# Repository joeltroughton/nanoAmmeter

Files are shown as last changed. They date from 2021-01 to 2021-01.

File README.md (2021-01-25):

# nanoAmmeter

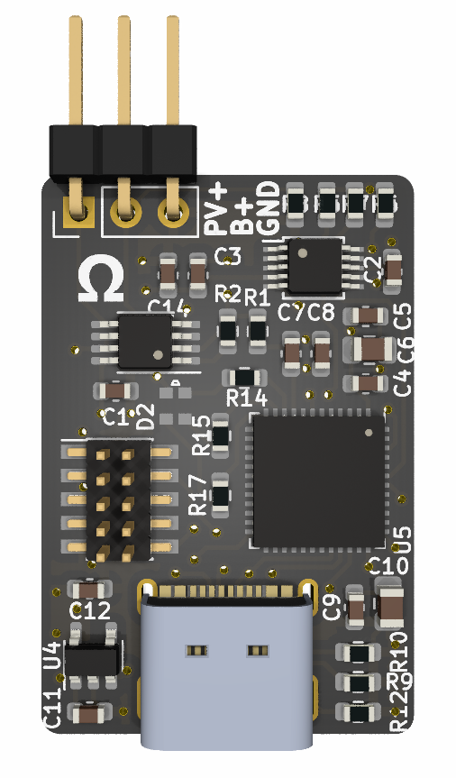
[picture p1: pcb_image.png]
nanoAmmeter


nanoAmmeter is a small research device designed to measure the voltage applied to, and the current flowing through biological glucose sensors on the order of 10s to 100s of nanoamps.

As glucose is detected by the sensor, its resistance changes. nanoAmmeter measures the current flow through the sensor for later analysis.

## Function

The nanoAmmeter is inserted between the biosensor's negative electrode and ground. The voltage drop across a 100kOhm resistor is amplified by a gain of 101 by a very low offset opamp (Analog LTC2055, ± 3 μV) and finally read by a 16-bit ADC (TI ADS1115). With a FSR of 4.096V, this gives us a theoretical current resolution of 12.4 pA. 

The voltage applied to the positive side of the biosensor is buffered to the ADC with unity gain for a theoretic voltage resolution of 125 μV.

The ADC is read by a STM32F072 MCU at 128 samples per second where it is fed into a finite impulse response, low pass filter and exported via USB. 

## Acknowledgments
Thanks to https://github.com/pms67 for the FIR circular buffer implementation

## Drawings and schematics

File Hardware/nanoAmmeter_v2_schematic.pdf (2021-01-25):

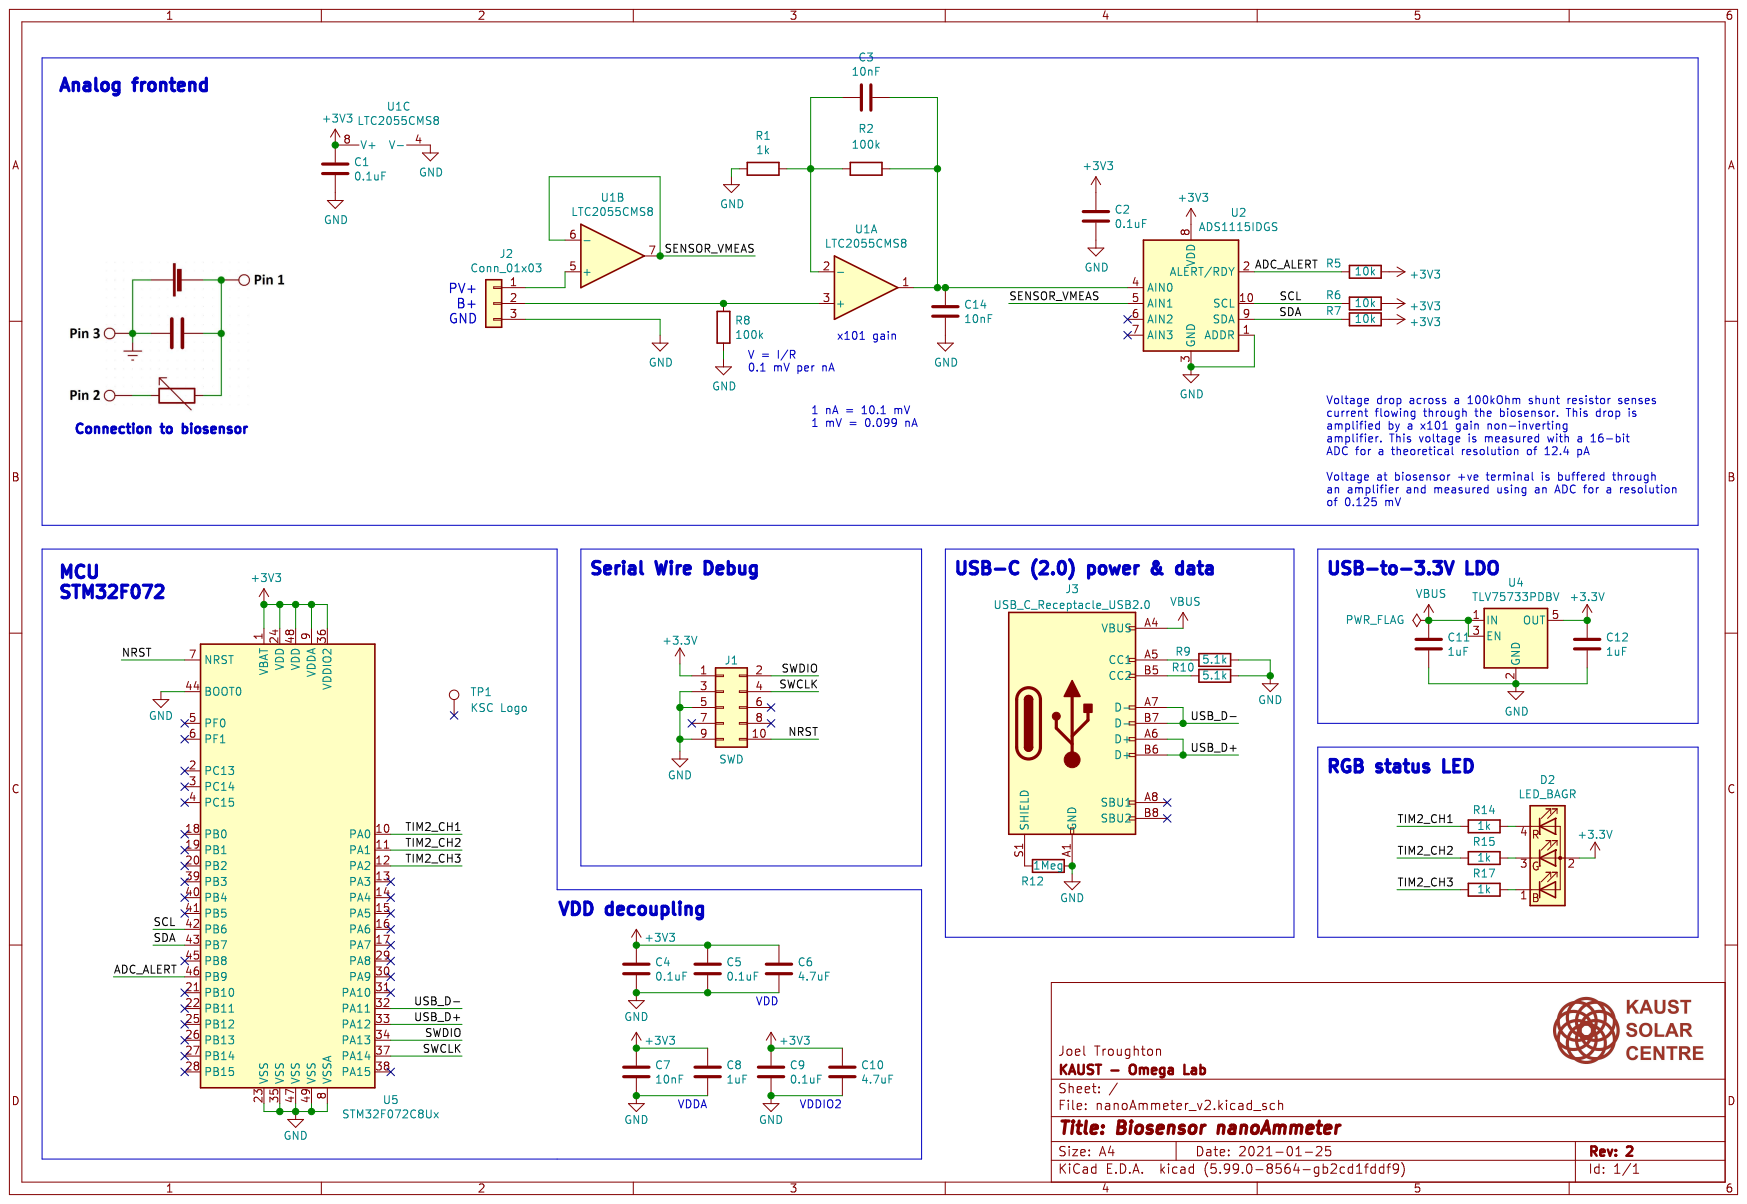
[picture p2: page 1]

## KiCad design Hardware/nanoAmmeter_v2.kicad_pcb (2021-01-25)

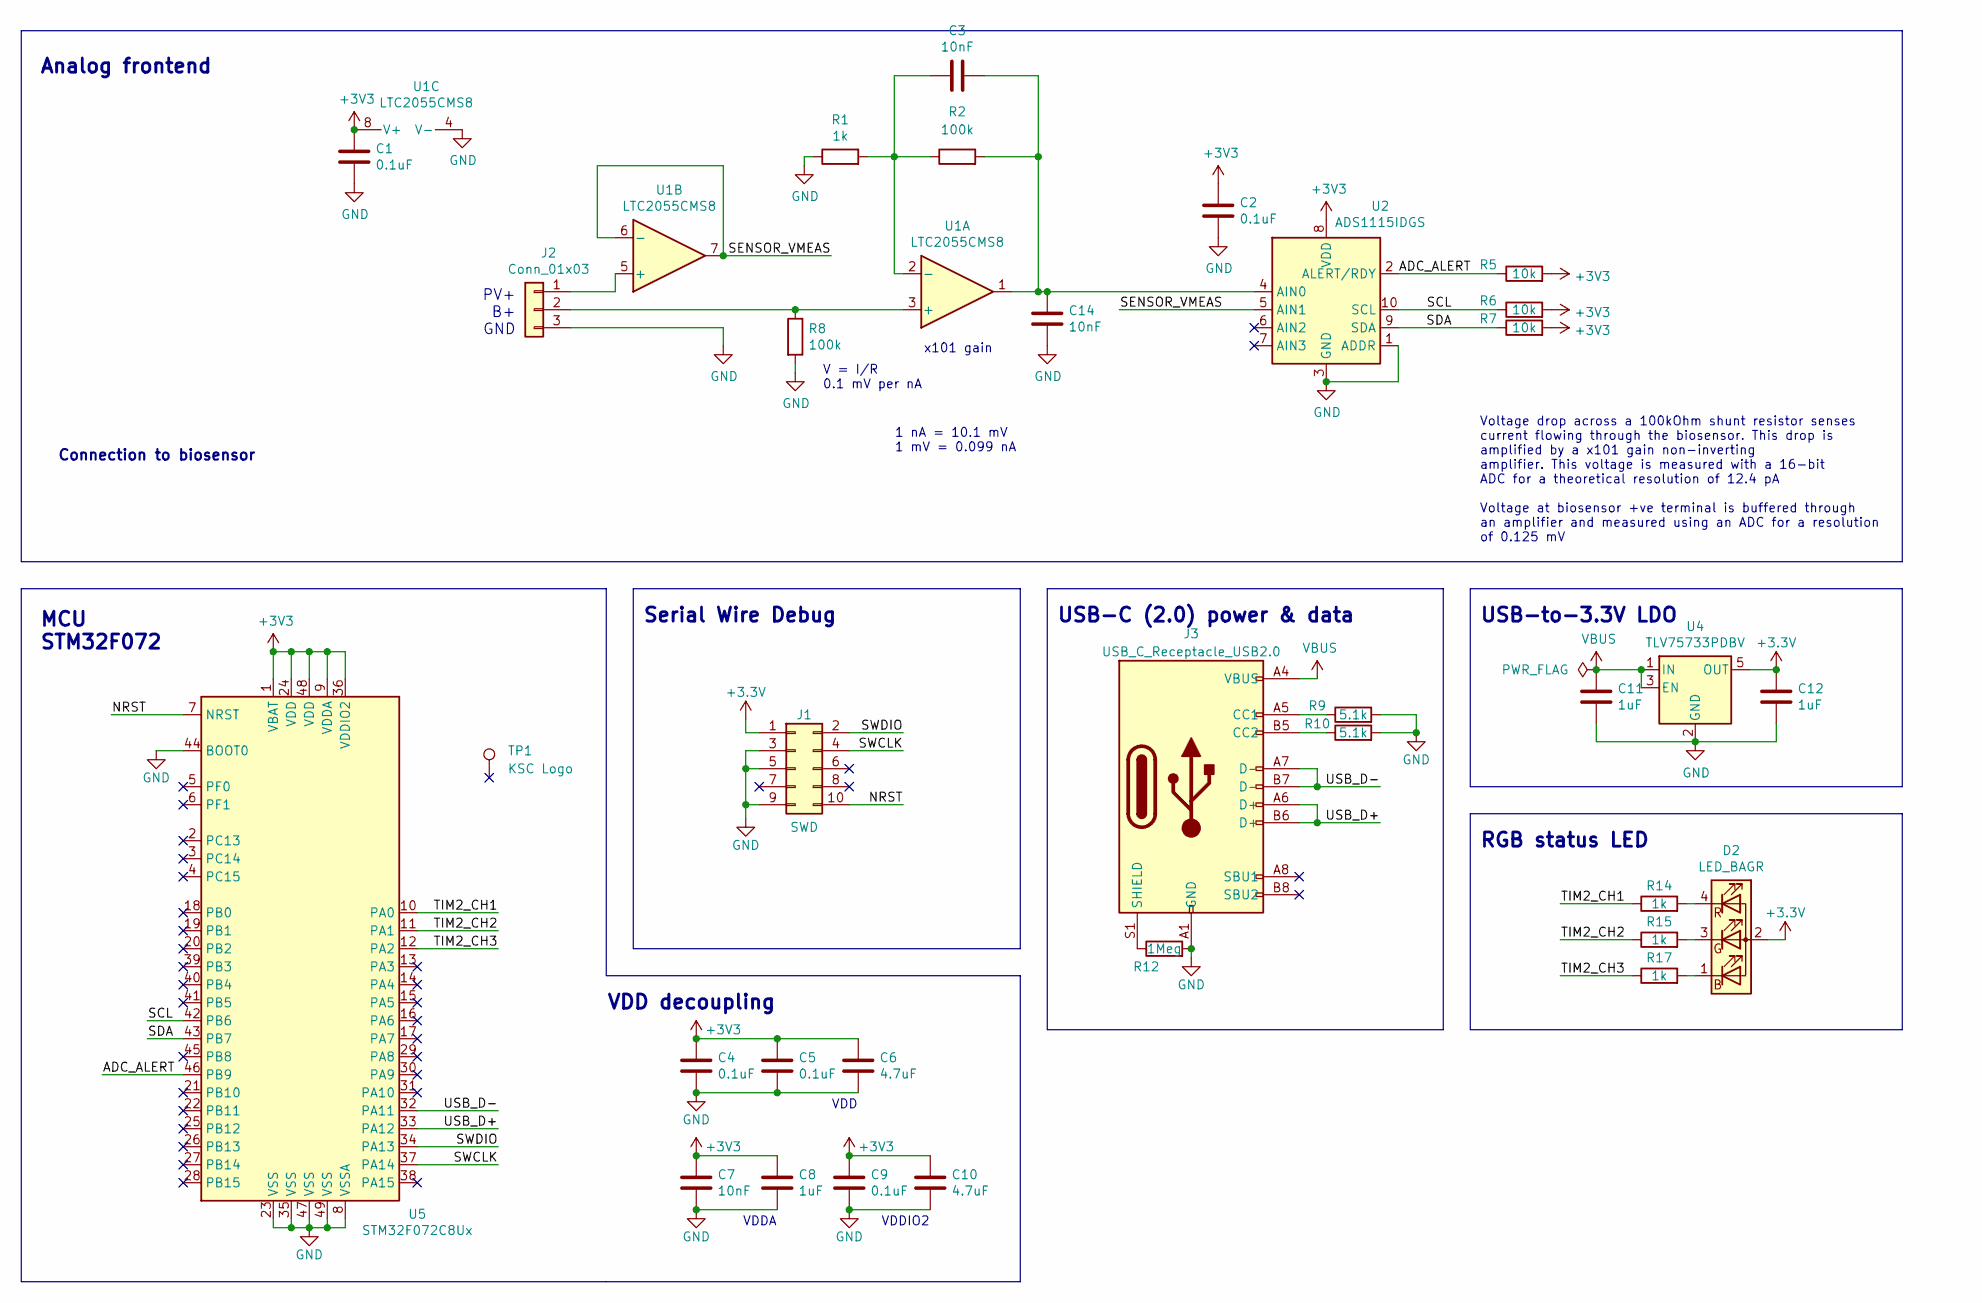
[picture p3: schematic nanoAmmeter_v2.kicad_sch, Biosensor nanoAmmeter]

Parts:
C1, C2, C4, C5, C9: 0.1uF; C_0603_1608Metric
C3, C7, C14: 10nF; C_0603_1608Metric
C6, C10: 4.7uF; C_0805_2012Metric
C8, C11, C12: 1uF; C_0603_1608Metric
D2: LED_BAGR; E6C0606RGBC3UDA
J1: SWD; PinHeader_2x05_P1.27mm_Vertical_SMD
J2: Conn_01x03; PinHeader_1x03_P2.54mm_Vertical
J3: USB_C_Receptacle_USB2.0; Molex_105450-0101
R1, R14, R15, R17: 1k; R_0603_1608Metric
R2, R8: 100k; R_0603_1608Metric
R5, R6, R7: 10k; R_0603_1608Metric
R9, R10: 5.1k; R_0603_1608Metric
R12: 1Meg; R_0603_1608Metric
TP1: KSC Logo; ksclogo
U1: LTC2055CMS8; MSOP-8_3x3mm_P0.65mm
U2: ADS1115IDGS; TSSOP-10_3x3mm_P0.5mm
U4: TLV75733PDBV; SOT-23-5
U5: STM32F072C8Ux; QFN-48-1EP_7x7mm_P0.5mm_EP5.6x5.6mm

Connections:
/ADC_ALERT: R5.1, U2.2 (ALERT/RDY), U5.46 (PB9)
/NRST: J1.10, U5.7 (NRST)
/SCL: R6.1, U2.10 (SCL), U5.42 (PB6)
/SDA: R7.1, U2.9 (SDA), U5.43 (PB7)
/SENSOR_VMEAS: U1.6 (-), U1.7, U2.5 (AIN1)
/SWCLK: J1.4, U5.37 (PA14)
/SWDIO: J1.2, U5.34 (PA13)
/TIM2_CH1: R14.1, U5.10 (PA0)
/TIM2_CH2: R15.1, U5.11 (PA1)
/TIM2_CH3: R17.1, U5.12 (PA2)
/USB_D+: J3.A6 (D+), J3.B6 (D+), U5.33 (PA12)
/USB_D-: J3.A7 (D-), J3.B7 (D-), U5.32 (PA11)
GND: C1.2, C2.2, C4.2, C5.2, C6.2, C7.2, C8.2, C9.2, C10.2, C11.2, C12.2, C14.2, J1.3, J1.5, J1.9, J2.3, J3.A1 (GND), J3.A12 (GND), J3.B1 (GND), J3.B12 (GND), R1.1, R8.2, R9.2, R10.2, R12.2, U1.4 (V-), U2.1 (ADDR), U2.3 (GND), U4.2 (GND), U5.8 (VSSA), U5.23 (VSS), U5.35 (VSS), U5.44 (BOOT0), U5.47 (VSS), U5.49 (VSS)
unnamed: C3.1, R1.2, R2.1, U1.2 (-)
unnamed: C3.2, C14.1, R2.2, U1.1, U2.4 (AIN0)
unnamed: D2.1 (BK), R17.2
unnamed: D2.3 (GK), R15.2
unnamed: D2.4 (RK), R14.2
unnamed: J2.1, U1.5 (+)
unnamed: J2.2, R8.1, U1.3 (+)
unnamed: J3.A5 (CC1), R9.1
unnamed: J3.B5 (CC2), R10.1
unnamed: J3.S1 (SHIELD), R12.1
VBUS: C11.1, J3.A4 (VBUS), J3.A9 (VBUS), J3.B4 (VBUS), J3.B9 (VBUS), U4.1 (IN), U4.3 (EN)
no_connect_26: J1.6
no_connect_27: J1.7
no_connect_28: J1.8
no_connect_29: J3.A8 (SBU1)
no_connect_30: J3.B8 (SBU2)
no_connect_32: U2.6 (AIN2)
no_connect_33: U2.7 (AIN3)
no_connect_34: U5.13 (PA3)
no_connect_35: U5.14 (PA4)
no_connect_36: U5.15 (PA5)
no_connect_37: U5.16 (PA6)
no_connect_38: U5.17 (PA7)
no_connect_39: U5.18 (PB0)
no_connect_40: U5.19 (PB1)
no_connect_41: U5.2 (PC13)
no_connect_42: U5.20 (PB2)
no_connect_43: U5.21 (PB10)
no_connect_44: U5.22 (PB11)
no_connect_45: U5.25 (PB12)
no_connect_46: U5.26 (PB13)
no_connect_47: U5.27 (PB14)
no_connect_48: U5.28 (PB15)
no_connect_49: U5.29 (PA8)
no_connect_50: U5.3 (PC14)
no_connect_51: U5.30 (PA9)
no_connect_52: U5.31 (PA10)
no_connect_53: U5.38 (PA15)
no_connect_54: U5.39 (PB3)
no_connect_55: U5.4 (PC15)
no_connect_56: U5.40 (PB4)
no_connect_57: U5.41 (PB5)
no_connect_58: U5.45 (PB8)
no_connect_59: U5.5 (PF0)
no_connect_60: U5.6 (PF1)

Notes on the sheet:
Analog frontend
MCU STM32F072
Connection to biosensor
PV+ B+ GND
VDD decoupling
Serial Wire Debug
VDDA
V = I/R 0.1 mV per nA
VDD
1 nA = 10.1 mV 1 mV = 0.099 nA
VDDIO2
x101 gain
USB-C (2.0) power & data
Voltage drop across a 100kOhm shunt resistor senses current flowing through the biosensor. This drop is amplified by a x101 gain non-inverting amplifier. This voltage is measured with a 16-bit ADC for a theoretical resolution of 12.4 pA Voltage at biosensor +ve terminal is buffered through an ampli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
USB-to-3.3V LDO
RGB status LED

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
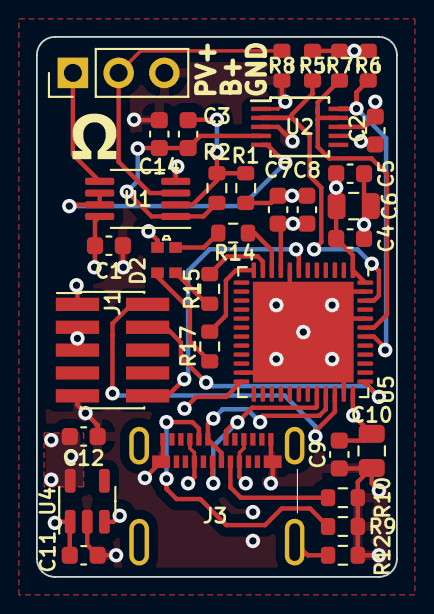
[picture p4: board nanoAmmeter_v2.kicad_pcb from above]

Board: 4 copper layers, 20.0 x 30.0 mm, 34 parts (1 on the bottom side), 25 nets.

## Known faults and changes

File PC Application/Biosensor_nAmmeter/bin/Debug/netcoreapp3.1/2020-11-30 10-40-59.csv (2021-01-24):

Time (ms) | PV cell voltage (mV) | Biosensor current (nA)
211 | 493 | 1181.375
406 | 489.5 | 1186.375
608 | 493.375 | 1191
811 | 490.75 | 1180
1014 | 490.125 | 1189.25
1217 | 493.625 | 1188.125
1421 | 489.875 | 1180.75
1624 | 492.125 | 1190.875
1826 | 493.5 | 1183
2031 | 489.5 | 1182
2233 | 493.125 | 1190.875
2436 | 492.375 | 1181.375
2639 | 489.5 | 1188.375
2843 | 493.5 | 1190.75
3046 | 490.375 | 1180
3248 | 490.625 | 1189.5
3452 | 493.75 | 1186.25
3654 | 489.75 | 1181
3859 | 492.5 | 1191.375
4061 | 493.25 | 1181.875
4263 | 489.5 | 1183.375
4468 | 493.25 | 1191.125
4670 | 491.25 | 1180.875
4873 | 489.75 | 1189.625
5076 | 493.625 | 1189.5
5280 | 490.125 | 1179.875
5483 | 491.25 | 1190.25
5686 | 493.75 | 1184.375
5888 | 489.625 | 1182.25
6092 | 492.875 | 1191.375
6295 | 493 | 1181.25
6499 | 489.375 | 1184.875
6701 | 493.375 | 1191.25
6904 | 491 | 1181.25
7108 | 489.875 | 1189.75
7310 | 493.625 | 1188.75
7514 | 490 | 1180.25
7717 | 491.625 | 1191.375
7919 | 493.625 | 1184
8123 | 489.625 | 1182
8327 | 492.875 | 1190.25
8529 | 492.875 | 1181.375
8733 | 489.375 | 1185.5
8935 | 493.375 | 1192
9139 | 491.125 | 1181.625
9342 | 489.875 | 1189.5
9545 | 493.625 | 1189.375
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

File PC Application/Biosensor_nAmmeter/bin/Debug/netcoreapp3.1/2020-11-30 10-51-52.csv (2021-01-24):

Time (ms) | PV cell voltage (mV) | Biosensor current (nA)
204 | 488.625 | 97.087
408 | 491.25 | 97.717
610 | 492.25 | 97.707
812 | 489.625 | 97.045
1018 | 488.625 | 97.293
1218 | 491.75 | 97.769
1423 | 492.375 | 97.521
1625 | 489.125 | 96.983
1827 | 488.75 | 97.541
2031 | 492.125 | 97.851
2236 | 492.125 | 97.293
2437 | 488.875 | 96.973
2642 | 489.375 | 97.603
2845 | 492.125 | 97.789
3046 | 491.75 | 97.211
3248 | 488.625 | 97.056
3452 | 490.25 | 97.686
3655 | 492.25 | 97.779
3859 | 491 | 97.097
4062 | 488.625 | 97.118
4264 | 490.875 | 97.769
4467 | 492.25 | 97.779
4671 | 490.125 | 97.035
4874 | 488.5 | 97.149
5080 | 491.375 | 97.8
5280 | 492.375 | 97.727
5482 | 489.625 | 97.056
5686 | 488.625 | 97.324
5888 | 491.75 | 97.758
6092 | 492.25 | 97.531
6295 | 489 | 97.056
6498 | 489 | 97.614
6701 | 492.125 | 97.81
6904 | 491.875 | 97.231
7108 | 488.75 | 97.004
7311 | 489.5 | 97.707
7514 | 492.25 | 97.851
7716 | 491.5 | 97.159
7920 | 488.625 | 97.014
8122 | 490.625 | 97.727
8326 | 492.25 | 97.81
8529 | 490.375 | 97.118
8732 | 488.625 | 97.149
8935 | 491.5 | 97.758
9137 | 492.375 | 97.655
9340 | 489.375 | 97.045
9544 | 488.625 | 97.407
9747 | 491.875 | 97.81
9950 | 492.25 | 97.438
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

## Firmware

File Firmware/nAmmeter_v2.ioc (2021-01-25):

#MicroXplorer Configuration settings - do not modify
File.Version=6
GPIO.groupedBy=Group By Peripherals
KeepUserPlacement=false
Mcu.Family=STM32F0
Mcu.IP0=I2C1
Mcu.IP1=NVIC
Mcu.IP2=RCC
Mcu.IP3=SYS
Mcu.IP4=USB
Mcu.IP5=USB_DEVICE
Mcu.IPNb=6
Mcu.Name=STM32F072C(8-B)Ux
Mcu.Package=UFQFPN48
Mcu.Pin0=PA0
Mcu.Pin1=PA1
Mcu.Pin2=PA2
Mcu.Pin3=PA11
Mcu.Pin4=PA12
Mcu.Pin5=PB6
Mcu.Pin6=PB7
Mcu.Pin7=PB9
Mcu.Pin8=VP_SYS_VS_Systick
Mcu.Pin9=VP_USB_DEVICE_VS_USB_DEVICE_CDC_FS
Mcu.PinsNb=10
Mcu.ThirdPartyNb=0
Mcu.UserConstants=
Mcu.UserName=STM32F072C8Ux
MxCube.Version=6.1.1
MxDb.Version=DB.6.0.10
NVIC.ForceEnableDMAVector=true
NVIC.HardFault_IRQn=true\:0\:0\:false\:false\:true\:false\:false
NVIC.NonMaskableInt_IRQn=true\:0\:0\:false\:false\:true\:false\:false
NVIC.PendSV_IRQn=true\:0\:0\:false\:false\:true\:false\:false
NVIC.SVC_IRQn=true\:0\:0\:false\:false\:true\:false\:false
NVIC.SysTick_IRQn=true\:0\:0\:false\:false\:true\:false\:true
NVIC.USB_IRQn=true\:0\:0\:false\:false\:true\:false\:true
PA0.GPIOParameters=GPIO_Label
PA0.GPIO_Label=LED_R
PA0.Locked=true
PA0.Signal=GPIO_Output
PA1.GPIOParameters=GPIO_Label
PA1.GPIO_Label=LED_G
PA1.Locked=true
PA1.Signal=GPIO_Output
PA11.Mode=Device
PA11.Signal=USB_DM
PA12.Mode=Device
PA12.Signal=USB_DP
PA2.GPIOParameters=GPIO_Label
PA2.GPIO_Label=LED_B
PA2.Locked=true
PA2.Signal=GPIO_Output
PB6.Mode=I2C
PB6.Signal=I2C1_SCL
PB7.Mode=I2C
PB7.Signal=I2C1_SDA
PB9.GPIOParameters=GPIO_Label
PB9.GPIO_Label=ADC_Alert
PB9.Locked=true
PB9.Signal=GPIO_Input
PinOutPanel.RotationAngle=0
ProjectManager.AskForMigrate=true
ProjectManager.BackupPrevious=false
ProjectManager.CompilerOptimize=6
ProjectManager.ComputerToolchain=false
ProjectManager.CoupleFile=false
ProjectManager.CustomerFirmwarePackage=
ProjectManager.DefaultFWLocation=true
ProjectManager.DeletePrevious=true
ProjectManager.DeviceId=STM32F072C8Ux
ProjectManager.FirmwarePackage=STM32Cube FW_F0 V1.11.2
ProjectManager.FreePins=false
ProjectManager.HalAssertFull=false
ProjectManager.HeapSize=0x200
ProjectManager.KeepUserCode=true
ProjectManager.LastFirmware=true
ProjectManager.LibraryCopy=1
ProjectManager.MainLocation=Core/Src
ProjectManager.NoMain=false
ProjectManager.PreviousToolchain=STM32CubeIDE
ProjectManager.ProjectBuild=false
ProjectManager.ProjectFileName=nAmmeter_v2.ioc
ProjectManager.ProjectName=nAmmeter_v2
ProjectManager.RegisterCallBack=
ProjectManager.StackSize=0x400
ProjectManager.TargetToolchain=STM32CubeIDE
ProjectManager.ToolChainLocation=
ProjectManager.UnderRoot=true
ProjectManager.functionlistsort=1-MX_GPIO_Init-GPIO-false-HAL-true,2-SystemClock_Config-RCC-false-HAL-false,3-MX_I2C1_Init-I2C1-false-HAL-true,4-MX_TIM2_Init-TIM2-false-HAL-true,5-MX_USB_DEVICE_Init-USB_DEVICE-false-HAL-false
RCC.AHBFreq_Value=48000000
RCC.APB1Freq_Value=48000000
RCC.APB1TimFreq_Value=48000000
RCC.CECFreq_Value=32786.88524590164
RCC.FCLKCortexFreq_Value=48000000
RCC.FamilyName=M
RCC.HCLKFreq_Value=48000000
RCC.HSICECFreq_Value=32786.88524590164
RCC.I2SFreq_Value=48000000
RCC.IPParameters=AHBFreq_Value,APB1Freq_Value,APB1TimFreq_Value,CECFreq_Value,FCLKCortexFreq_Value,FamilyName,HCLKFreq_Value,HSICECFreq_Value,I2SFreq_Value,MCOFreq_Value,PLLCLKFreq_Value,PLLMCOFreq_Value,SYSCLKFreq_VALUE,SYSCLKSource,TimSysFreq_Value,USART1Freq_Value,USART2Freq_Value,VCOOutput2Freq_Value
RCC.MCOFreq_Value=48000000
RCC.PLLCLKFreq_Value=16000000
RCC.PLLMCOFreq_Value=16000000
RCC.SYSCLKFreq_VALUE=48000000
RCC.SYSCLKSource=RCC_SYSCLKSOURCE_HSI48
RCC.TimSysFreq_Value=48000000
RCC.USART1Freq_Value=48000000
RCC.USART2Freq_Value=48000000
RCC.VCOOutput2Freq_Value=8000000
USB_DEVICE.CLASS_NAME_FS=CDC
USB_DEVICE.IPParameters=VirtualMode,VirtualModeFS,CLASS_NAME_FS
USB_DEVICE.VirtualMode=Cdc
USB_DEVICE.VirtualModeFS=Cdc_FS
VP_SYS_VS_Systick.Mode=SysTick
VP_SYS_VS_Systick.Signal=SYS_VS_Systick
VP_USB_DEVICE_VS_USB_DEVICE_CDC_FS.Mode=CDC_FS
VP_USB_DEVICE_VS_USB_DEVICE_CDC_FS.Signal=USB_DEVICE_VS_USB_DEVICE_CDC_FS
board=custom
isbadioc=false

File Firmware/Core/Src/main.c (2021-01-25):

/* USER CODE BEGIN Header */
/*
 * nanoAmmeter version 2
 *
 * Joel Troughton 2021
 * working at the KAUST Solar Center
 *
 * Credit to Phil Salmony (philsal.co.uk) for the FIR code
 */


/* USER CODE END Header */
/* Includes ------------------------------------------------------------------*/
#include "main.h"
#include "usb_device.h"

/* Private includes ----------------------------------------------------------*/
/* USER CODE BEGIN Includes */
#include "usbd_cdc_if.h"
#include "stdbool.h"
#include "FIRFilter.h"
/* USER CODE END Includes */

/* Private typedef -----------------------------------------------------------*/
/* USER CODE BEGIN PTD */
#define ADS1115_ADDRESS 0x48 // I2C addresses of ADC
/* USER CODE END PTD */

/* Private define ------------------------------------------------------------*/
/* USER CODE BEGIN PD */
/* USER CODE END PD */

/* Private macro -------------------------------------------------------------*/
/* USER CODE BEGIN PM */

/* USER CODE END PM */

/* Private variables ---------------------------------------------------------*/
I2C_HandleTypeDef hi2c1;

/* USER CODE BEGIN PV */
extern USBD_HandleTypeDef hUsbDeviceFS;

uint8_t UserRxBuffer[2048];
bool usbMessageReceived = false;

bool streaming_data_requested = false;

float amp_gain = 101;
float shunt_resistance = 100000;

// FIR filters for both voltage and current
FIRFilter lpfcurr;
FIRFilter lpfvolt;

/* USER CODE END PV */

/* Private function prototypes -----------------------------------------------*/
void SystemClock_Config(void);
static void MX_GPIO_Init(void);
static void MX_I2C1_Init(void);
/* USER CODE BEGIN PFP */

/* USER CODE END PFP */

/* Private user code ---------------------------------------------------------*/
/* USER CODE BEGIN 0 */

// Initialise the ADS1115 at boot. Sets the comparator to toggle the alert pin
// when a measurement is completed
void adc_init()
{
	uint8_t conversion_reg = 0x00;
	uint8_t config_reg = 0x01;
	uint8_t lothresh_reg = 0x02;
	uint8_t hithresh_reg = 0x03;

	unsigned char ADSwrite[6];

	ADSwrite[0] = hithresh_reg;
	ADSwrite[1] = 0x80;
	ADSwrite[2] = 0x00;
	HAL_I2C_Master_Transmit(&hi2c1, ADS1115_ADDRESS << 1, ADSwrite, 3, 100);

	ADSwrite[0] = lothresh_reg;
	ADSwrite[1] = 0x7F;
	ADSwrite[2] = 0xFF;
	HAL_I2C_Master_Transmit(&hi2c1, ADS1115_ADDRESS << 1, ADSwrite, 3, 100);
}

/* Make a single-ended ADC measurement. Fixed at 128sps, 4.096V FSR
 *
 * For ADC registers:
 * https://www.ti.com/lit/ds/symlink/ads1115.pdf
 */
uint16_t adc_read_singleended(uint8_t channel)
{
	uint8_t conversion_reg = 0x00;
	uint8_t config_reg = 0x01;
	uint8_t lothresh_reg = 0x02;
	uint8_t hithresh_reg = 0x03;

	unsigned char ADSwrite[6];
	int16_t reading;

	switch (channel)
	{
	case 0:
		ADSwrite[1] = 0xC3;
		break;
	case 1:
		ADSwrite[1] = 0xD3;
		break;
	case 2:
		ADSwrite[1] = 0xE3;
		break;
	case 3:
		ADSwrite[1] = 0xF3;
		break;
	}

	HAL_GPIO_WritePin(GPIOA, LED_R_Pin, GPIO_PIN_SET);
	HAL_GPIO_WritePin(GPIOA, LED_G_Pin, GPIO_PIN_SET);
	HAL_GPIO_WritePin(GPIOA, LED_B_Pin, GPIO_PIN_SET);

	ADSwrite[0] = config_reg;
	ADSwrite[2] = 0b10001000; // For Alert pin, set COMP_QUE to anything but 11. Active low

	HAL_I2C_Master_Transmit(&hi2c1, ADS1115_ADDRESS << 1, ADSwrite, 3, 100);

	// Wait for ADC_Alert pin to go high, indicating the measurement is complete
	while (HAL_GPIO_ReadPin(ADC_Alert_GPIO_Port, ADC_Alert_Pin) == 0)
	{
		HAL_GPIO_WritePin(GPIOA, LED_B_Pin, GPIO_PIN_RESET);
	}

	HAL_GPIO_WritePin(GPIOA, LED_B_Pin, GPIO_PIN_SET);

	ADSwrite[0] = conversion_reg;

	HAL_I2C_Master_Transmit(&hi2c1, ADS1115_ADDRESS << 1, ADSwrite, 1, 100);

	HAL_I2C_Master_Receive(&hi2c1, ADS1115_ADDRESS << 1, ADSwrite, 2, 100);
	reading = (ADSwrite[0] << 8 | ADSwrite[1]);
	if (reading < 0) // Shouldn't be any -ve values
	{
		reading = 0;
	}
	return reading;
}

void single_shot()
{
	//uint16_t v_measure = adc_read_singleended(1);
	//uint16_t i_measure = adc_read_singleended(0);

	//float voltage = (v_measure * 0.125);
	//float current = (i_measure * 0.125) / amp_gain / 0.1;

	float voltage_running = 0;
	float current_running = 0;

	for (int i = 0; i < num_oversamples; i++)
	{
		uint16_t v_measure = adc_read_singleended(1);
		uint16_t i_measure = adc_read_singleended(0);

		/*		float voltage = (v_measure * 0.000625) - 8.190538;
		 float current = (i_measure * 0.125 / 1000) / shunt_resistance
		 / i_amp_gain;
		 current = current + ((3.44E-5 * voltage) - 7.35E-5);*/

		/*		float voltage = v_measure * 0.125;
		 voltage = voltage / 1000;
		 voltage = voltage * 3.9947;
		 voltage = voltage - 6.1312;*/

		float voltage = v_measure * 0.125;
		float current = (i_measure * 0.125) / amp_gain / 0.1;

		voltage_running += voltage;
		current_running += current;
	}

	voltage_running /= num_oversamples;
	current_running /= num_oversamples;

	char vmsg[32];
	char imsg[32];

	memset(vmsg, 0, sizeof(vmsg));
	memset(imsg, 0, sizeof(imsg));

	sprintf(vmsg, "%4.3f", voltage_running);
	sprintf(imsg, "%4.3f", current_running);

	strcat(vmsg, ",");
	strcat(vmsg, imsg);

	strcat(vmsg, "\n");
	CDC_Transmit_FS(vmsg, sizeof(vmsg));
}

/* When the measurement is first started, the output creeps up
 * until the buffer is full. This fills the buffer up before
 * outputting any messages over USB
 */
void fill_fir_buffer()
{
	uint8_t filter_length = FIRFilter_FilterLength(&lpfcurr);

	for (uint8_t n = 0; n <= filter_length; n++)
	{
		uint16_t v_measure = adc_read_singleended(1);
		float voltage = v_measure * 0.125;

		uint16_t i_measure = adc_read_singleended(0);
		float current = (i_measure * 0.125) / amp_gain / 0.1;

		FIRFilter_Update(&lpfvolt, voltage);
		FIRFilter_Update(&lpfcurr, current);
	}
}

// Start outputting data
void run_fir()
{
	uint16_t v_measure = adc_read_singleended(1);
	float voltage = v_measure * 0.125;

	uint16_t i_measure = adc_read_singleended(0);
	float current = (i_measure * 0.125) / amp_gain / 0.1;

	FIRFilter_Update(&lpfvolt, voltage);
	FIRFilter_Update(&lpfcurr, current);

	char vmsg[32];
	char imsg[32];

	memset(vmsg, 0, sizeof(vmsg));
	memset(imsg, 0, sizeof(imsg));

	sprintf(vmsg, "%4.3f", lpfvolt.out);
	sprintf(imsg, "%4.3f", lpfcurr.out);

	strcat(vmsg, ",");
	strcat(vmsg, imsg);

	strcat(vmsg, "\n");
	CDC_Transmit_FS(vmsg, sizeof(vmsg));

}
/* USER CODE END 0 */

/**
 * @brief  The application entry point.
 * @retval int
 */
int main(void)
{
	/* USER CODE BEGIN 1 */

	/* USER CODE END 1 */

	/* MCU Configuration--------------------------------------------------------*/

	/* Reset of all peripherals, Initializes the Flash interface and the Systick. */
	HAL_Init();

	/* USER CODE BEGIN Init */

	/* USER CODE END Init */

	/* Configure the system clock */
	SystemClock_Config();

	/* USER CODE BEGIN SysInit */

	/* USER CODE END SysInit */

	/* Initialize all configured peripherals */
	MX_GPIO_Init();
	MX_I2C1_Init();
	MX_USB_DEVICE_Init();
	/* USER CODE BEGIN 2 */

	adc_init();
	FIRFilter_Init(&lpfcurr);
	FIRFilter_Init(&lpfvolt);

	/* USER CODE END 2 */

	/* Infinite loop */
	/* USER CODE BEGIN WHILE */
	while (1)
	{
		/* USER CODE END WHILE */

		HAL_GPIO_WritePin(GPIOA, LED_R_Pin, GPIO_PIN_SET);
		HAL_GPIO_WritePin(GPIOA, LED_G_Pin, GPIO_PIN_RESET);
		HAL_GPIO_WritePin(GPIOA, LED_B_Pin, GPIO_PIN_SET);

		if (streaming_data_requested)
		{
			run_fir();
		}

		if (usbMessageReceived == true)
		{

			char chRxBuffer[2048];

			// Take the uint8_t buffer and turn it into a char array to parse
			for (int i = 0; i <= 2048; i++)
			{
				chRxBuffer[i] = UserRxBuffer[i];
			}

			usbMessageReceived = false; // Wait untill we have read the incoming message

			char singleshotSearch[] = "single"; 	// Take a single shot
			char startSearch[] = "start"; 			// Begin continuous measurements
			char stopSearch[] = "stop";				// Stop continuous measurements

			char *singleshotPtr = strstr(chRxBuffer, singleshotSearch);
			char *startPtr = strstr(chRxBuffer, startSearch);
			char *stopPtr = strstr(chRxBuffer, stopSearch);

			if (singleshotPtr != NULL)
			{
				run_fir();
			}
			else if (startPtr != NULL)
			{
				streaming_data_requested = true;
				fill_fir_buffer();

			}
			else if (stopPtr != NULL) // Do a little stop light blink
			{
				streaming_data_requested = false;

				HAL_GPIO_WritePin(GPIOA, LED_R_Pin, GPIO_PIN_RESET);
				HAL_GPIO_WritePin(GPIOA, LED_G_Pin, GPIO_PIN_SET);
				HAL_GPIO_WritePin(GPIOA, LED_B_Pin, GPIO_PIN_SET);

				HAL_Delay(100);

				HAL_GPIO_WritePin(GPIOA, LED_R_Pin, GPIO_PIN_SET);
				HAL_GPIO_WritePin(GPIOA, LED_G_Pin, GPIO_PIN_SET);
				HAL_GPIO_WritePin(GPIOA, LED_B_Pin, GPIO_PIN_SET);

				HAL_Delay(50);

				HAL_GPIO_WritePin(GPIOA, LED_R_Pin, GPIO_PIN_RESET);
				HAL_GPIO_WritePin(GPIOA, LED_G_Pin, GPIO_PIN_SET);
				HAL_GPIO_WritePin(GPIOA, LED_B_Pin, GPIO_PIN_SET);

				HAL_Delay(100);

				HAL_GPIO_WritePin(GPIOA, LED_R_Pin, GPIO_PIN_SET);
				HAL_GPIO_WritePin(GPIOA, LED_G_Pin, GPIO_PIN_SET);
				HAL_GPIO_WritePin(GPIOA, LED_B_Pin, GPIO_PIN_SET);

				HAL_Delay(100);

				HAL_GPIO_WritePin(GPIOA, LED_R_Pin, GPIO_PIN_SET);
				HAL_GPIO_WritePin(GPIOA, LED_G_Pin, GPIO_PIN_RESET);
				HAL_GPIO_WritePin(GPIOA, LED_B_Pin, GPIO_PIN_SET);

			}
			else
			{
				char msg[1024] = "Input not understood";
				strcat(msg, "\n");
				CDC_Transmit_FS(msg, sizeof(msg));
			}
		}
		/* USER CODE BEGIN 3 */
	}
	/* USER CODE END 3 */
}

/**
 * @brief System Clock Configuration
 * @retval None
 */
void SystemClock_Config(void)
{
	RCC_OscInitTypeDef RCC_OscInitStruct =
	{ 0 };
	RCC_ClkInitTypeDef RCC_ClkInitStruct =
	{ 0 };
	RCC_PeriphCLKInitTypeDef PeriphClkInit =
	{ 0 };

	/** Initializes the RCC Oscillators according to the specified parameters
	 * in the RCC_OscInitTypeDef structure.
	 */
	RCC_OscInitStruct.OscillatorType = RCC_OSCILLATORTYPE_HSI
			| RCC_OSCILLATORTYPE_HSI48;
	RCC_OscInitStruct.HSIState = RCC_HSI_ON;
	RCC_OscInitStruct.HSI48State = RCC_HSI48_ON;
	RCC_OscInitStruct.HSICalibrationValue = RCC_HSICALIBRATION_DEFAULT;
	RCC_OscInitStruct.PLL.PLLState = RCC_PLL_NONE;
	if (HAL_RCC_OscConfig(&RCC_OscInitStruct) != HAL_OK)
	{
		Error_Handler();
	}
	/** Initializes the CPU, AHB and APB buses clocks
	 */
	RCC_ClkInitStruct.ClockType = RCC_CLOCKTYPE_HCLK | RCC_CLOCKTYPE_SYSCLK
			| RCC_CLOCKTYPE_PCLK1;
	RCC_ClkInitStruct.SYSCLKSource = RCC_SYSCLKSOURCE_HSI48;
	RCC_ClkInitStruct.AHBCLKDivider = RCC_SYSCLK_DIV1;
	RCC_ClkInitStruct.APB1CLKDivider = RCC_HCLK_DIV1;

	if (HAL_RCC_ClockConfig(&RCC_ClkInitStruct, FLASH_LATENCY_1) != HAL_OK)
	{
		Error_Handler();
	}
	PeriphClkInit.PeriphClockSelection = RCC_PERIPHCLK_USB | RCC_PERIPHCLK_I2C1;
	PeriphClkInit.I2c1ClockSelection = RCC_I2C1CLKSOURCE_HSI;
	PeriphClkInit.UsbClockSelection = RCC_USBCLKSOURCE_HSI48;

	if (HAL_RCCEx_PeriphCLKConfig(&PeriphClkInit) != HAL_OK)
	{
		Error_Handler();
	}
}
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

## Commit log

2021-01-25 Added PCB hardware files
    [2020-11-30 10-40-59.csv, 2020-11-30 10-51-52.csv, nanoAmmeter_v2-B_Cu.gbr, nanoAmmeter_v2-B_Mask.gbr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]
2021-01-25 Added image of PCB for readme
2021-01-25 Moved companion application to seperate folder
    [2020-11-30 10-40-59.csv, 2020-11-30 10-51-52.csv]
2021-01-25 Added STM32 firmware code

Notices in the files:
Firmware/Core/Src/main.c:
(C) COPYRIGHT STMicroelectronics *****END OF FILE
